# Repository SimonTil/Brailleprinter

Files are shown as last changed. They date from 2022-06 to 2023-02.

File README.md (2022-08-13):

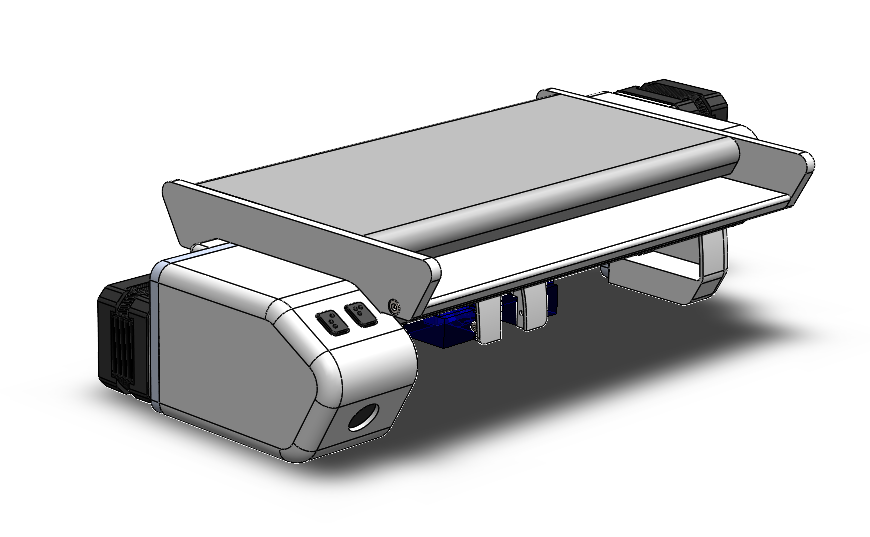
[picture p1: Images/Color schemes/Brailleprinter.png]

# Project brailleprinter
_Versie 1.0 door Simon Tillema_

Nederland kent zo'n 250.000 mensen met een visuele beperking. Ongeveer 3000 mensen gebruiken braille om te communiceren.
Tegenwoordig zijn de digitale middelen voor deze groep mensen enorm, waardoor braille op papier niet veel meer voorkomt.
Het gevolg daarvan is dat middelen om braille te 'schrijven' beperkt zijn. Braille op papier wordt voornamelijk gebruikt
waar digitale middelen (zoals brailleleesregel) niet toegepast kunnen worden. Denk daarbij aan stukken tekst die tijdens
een speciale gebeurtenis voorgelezen moeten worden, muziekteksten om te zingen, (liefdes)brieven, boeken, gedichten etc.    
Het 'schrijven' van braille op papier kan op 3 manieren:
1. met een reglette en prikpen;
2. met een brailletypemachine;
3. met een brailleprinter.

De focus binnen dit project ligt op die laatste. Commercieel beschikbare brailleprinters beginnen zo rond de €3000,- Dat
is voor de particulier praktisch onbetaalbaar. Daarom is besloten een goedkope open source brailleprinter op de markt te
zetten. Met een waarde van ongeveer een tiende van commercieel verkrijgbare apparaten is dit een echte game-changer. Het
apparaat moet door ieder die een beetje technische aanleg heeft in elkaar gezet kunnen worden.

## Hoe werkt de brailleprinter
De brailleprinter wordt geleverd met een softwarepakket dat teksten naar de brailleprinter stuurt. Daarmee kan men tekst
omzetten in braille en uit laten printen.
### Brailleprinter aansluiten
De brailleprinter bevat twee kabels: een stroomkabel, die 12V (48W) vraagt, en een USB-kabel naar de computer. De kabels
zitten niet strak vast in de brailleprinter. Belangrijk is dus om er niet te hard aan te trekken. Steek de stroomadapter
in het stopcontact en de USB-kabel in de computer. Vervolgens kan het programma gestart worden. Wanneer de kabel niet op
de computer is aangesloten, draait het programma wel, maar kan logischerwijs niet geprint worden. Zodra de stroomadapter
is aangesloten, geeft de printer een piepje. Nog een piepje klinkt als de USB-kabel wordt aangesloten. De brailleprinter
is nu klaar voor gebruik.
### Programma installeren
Moet nog gedaan worden!

## Licentie
(NL) Dit project is gelicenseerd onder de Creative Commons licentie (CC BY-NC-SA). Dat houdt in:  
Je bent vrij om:  
- **het werk te delen** - te kopiëren, te verspreiden en door te geven via elk medium of bestandsformaat;  
- **het werk te bewerken** - te remixen, te veranderen en afgeleide werken te maken.  

onder de volgende voorwaarden:  
- **Naamsvermelding:** De gebruiker dient de maker van het werk te vermelden, een link naar de licentie te plaatsen en aan
te geven of het werk veranderd is. Je mag dat op redelijke wijze doen, maar niet zodanig dat de indruk gewekt wordt dat
de licentiegever instemt met je werk of je gebruik van het werk;  
- **NietCommercieel:** Je mag het werk niet gebruiken voor commerciële doeleinden;  
- **GelijkDelen:** Als je het werk hebt geremixt, veranderd, of op het werk hebt voortgebouwd, moet je het veranderde
materiaal verspreiden onder dezelfde licentie als het originele werk;   
- **Geen aanvullende restricties:** Je mag geen juridische voorwaarden of technologische voorzieningen toepassen die
anderen er juridisch in beperken om iets te doen wat de licentie toestaat.  

_Zie ook de [website van Creative Commons](https://creativecommons.org/licenses/by-nc-sa/3.0/nl/deed.nl)._  

(EN) This project is licensed under the Creative Commons License (CC BY-NC-SA). That means:  
you are free to:  
- **Share** - copy and redistribute the material in any medium or format;  
- **Adapt** - remix, transform, and build upon the material.  

under the following terms:  
- **Attribution:** You must give appropriate credit, provide a link to the license, and indicate if changes were made. You
may do so in any reasonable manner, but not in any way that suggests the licensor endorses you or your use;  
- **NonCommercial:** You may not use the material for commercial purposes;  
- **ShareAlike:** If you remix, transform, or build upon the material, you must distribute your contributions under the same
license as the original;  
- **No additional restrictions:** You may not apply legal terms or technological measures that legally restrict others from
doing anything the license permits.  

_See also the [website of Creative Commons](https://creativecommons.org/licenses/by-nc-sa/3.0/nl/deed.en)._  

## Help de ontwikkeling 
Vindt u dit een mooi project en wilt u helpen om dit project een toekomst te geven? Dat kan!
Bent u handig met programmeren (C++/C#), 3D-tekenen (SolidWorks), prototypen, of PCB-design? Neem dan gerust contact op,
zodat we samen kunnen kijken wat u kunt betekenen voor dit project.  
Wilt u helpen, maar bent u niet technisch aangelegd? Geen probleem! Daar is ook een oplossing voor! Middels een (kleine)
financiële bijdrage kunnen de ontwikkelaars meer tijd vrijmaken om te werken aan dit project! Overmaken kan via de link:
[paypal.me/drawingsimon](paypal.me/drawingsimon).  
Licentie: dit project is gelicenseerd onder de Creative Commons licentie (CC BY-NC-SA) en mag, met vermelding van auteur
onder dezelfde licentie niet-commercieel gebruikt worden.  
Ik verzoek u vriendelijk de auteur op de hoogte te stellen van het gebruik van (delen van) het project, bijvoorbeeld via
een e-mail aan [simontillema@gmail.com](mailto:simontillema@gmail.com), of op andere wijze.

## Met dank aan
Mijn speciale dank gaat uit naar mijn vriendin Anne die mij geweldig heeft gesteund in dit project.  
Verder wil ik Michael bedanken die mij meerdere malen wist te motiveren om door te gaan.

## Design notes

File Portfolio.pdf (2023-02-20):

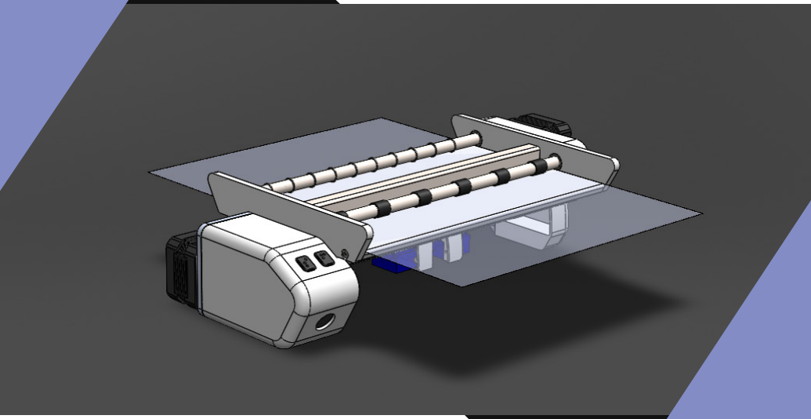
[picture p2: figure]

# PROJECT BRAILLE PRINTER

Sept. 16, 2022 | By Simon Tillema

### PAGE

# A Braille Printer?

### Commercially available braille printers are expensive and often large in

size. There are just a few open-source models available, which are large, slow, unreliable, and do not produce clear braille.

### The model I developed is better in all respects. it can print all six dots at once; it prints clearly readable braille; is very reliable and is built as compact as possible. With a simple computer program, everyone can use the

plug-and-play printer.

### I also developed this braille printer for my fiancée in light of her visual impairment. This apparatus makes it easier for me to have written communication with her. Her feedback was indispensable throughout the develop-

ment process.

### The first text printed (with the first prototype) for my girlfriend was some-

thing along the lines of Do you want to marry me? Fortunately she said YES.

You can follow this project on GitHub! https://github.com/SimonTil/Brailleprinter

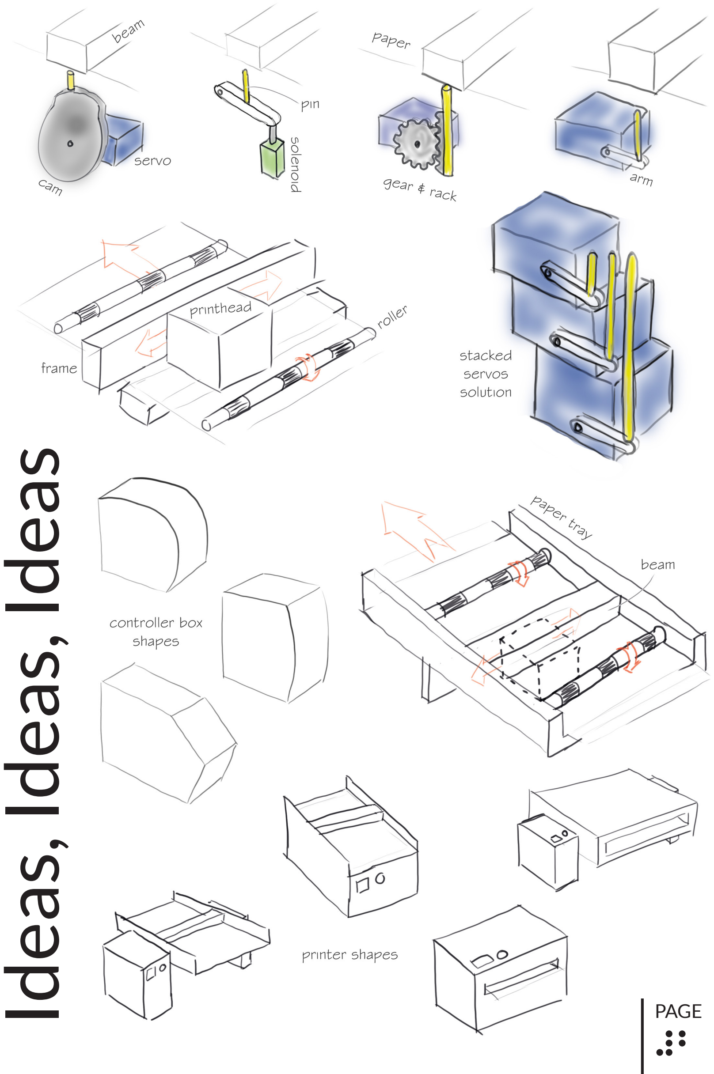
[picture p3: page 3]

# Ideas, Ideas, Ideas

### PAGE PAGE

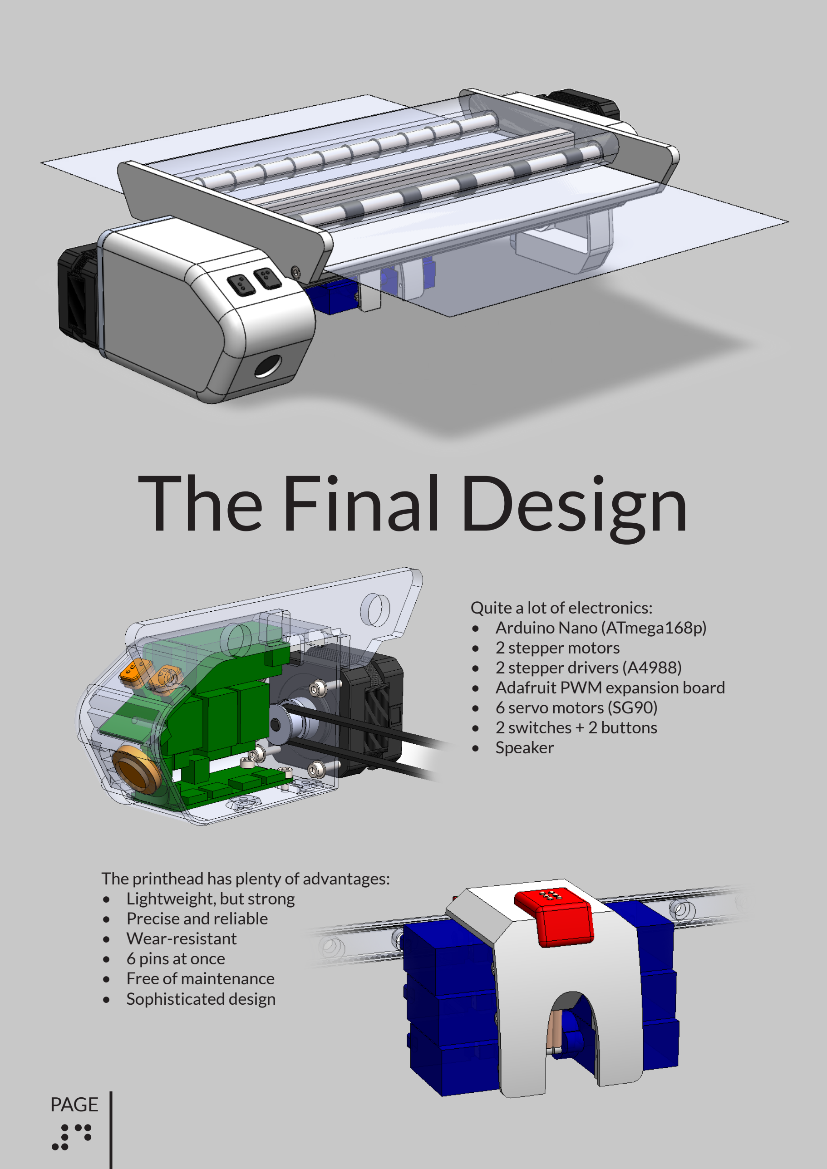
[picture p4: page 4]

Quite a lot of electronics:
- Arduino Nano (ATmega168p)
- 2 stepper motors
- 2 stepper drivers (A4988)
- Adafruit PWM expansion board
- 6 servo motors (SG90)
- 2 switches + 2 buttons
- Speaker

The printhead has plenty of advantages:
- Lightweight, but strong
- Precise and reliable
- Wear-resistant
- 6 pins at once
- Free of maintenance
- Sophisticated design

# The Final Design

# PAGEManufacturing

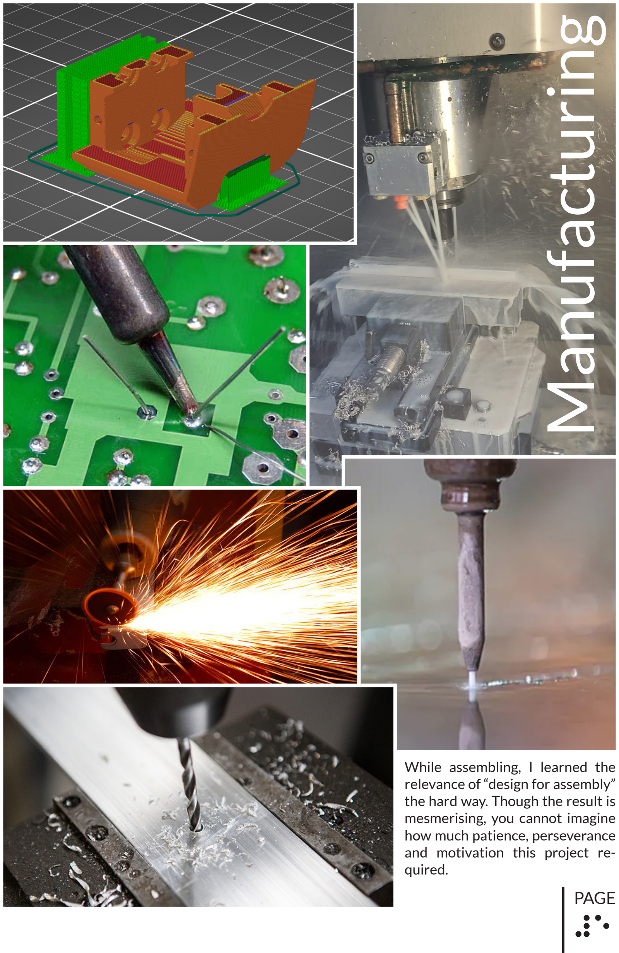
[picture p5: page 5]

While assembling, I learned the relevance of “design for assembly” the hard way. Though the result is mesmerising, you cannot imagine how much patience, perseverance and motivation this project re

quired.

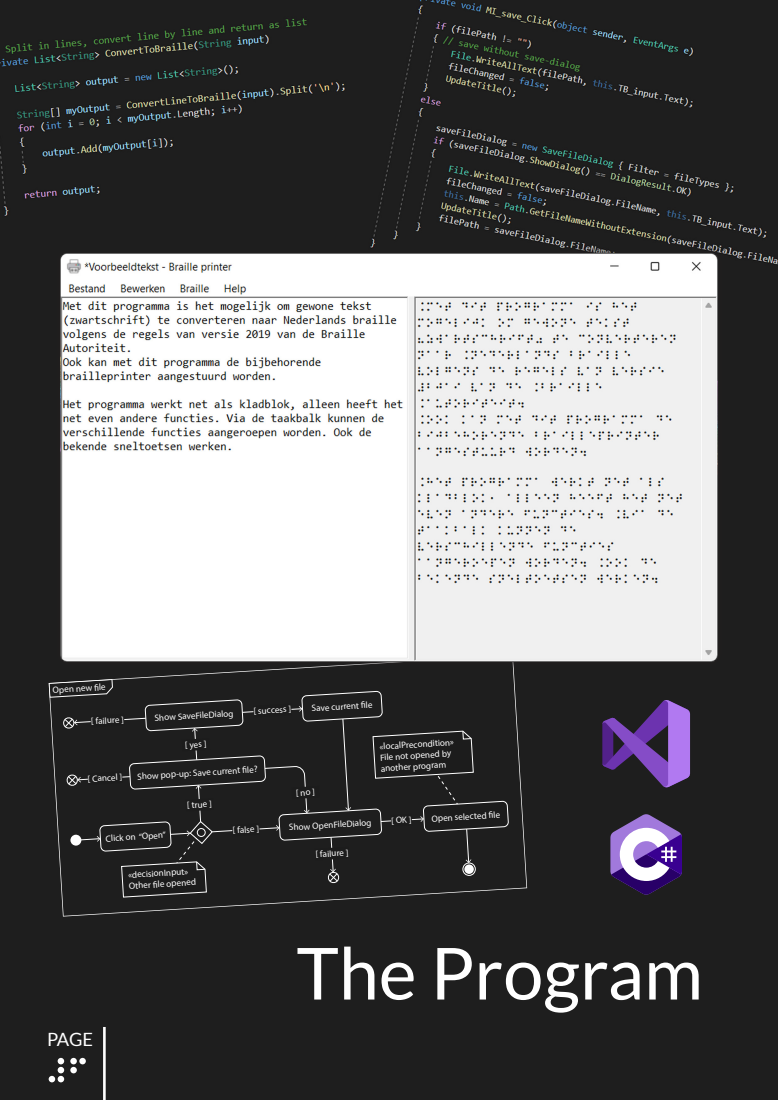
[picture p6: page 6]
«decisionInput»; [ true ]; [ Cancel ]; Show SaveFileDialog; [ yes ]; [ failure ]; «localPrecondition»; another program; The Program

Open new le

Save current le [ success ]

File not opened by

Show pop-up: Save current le?

[ OK ] Open selected le

Show OpenFileDialog [ false ]

Click on “Open”

Other le opened

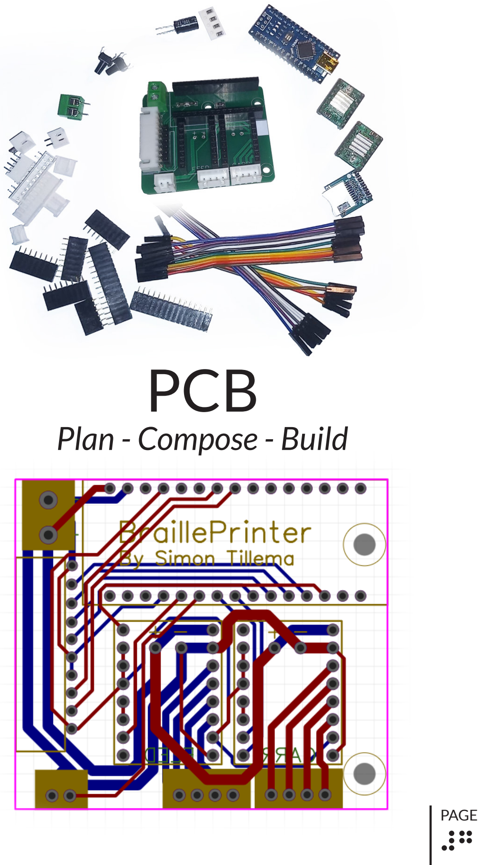
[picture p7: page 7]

# PCB

# Plan - Compose - Build

# Never Give Up!

Servos became glowing hot!
Due to the incorrect power supply, way too much current was provided to the servos, causing them to overheat. The temperature was far beyond the safe operation temperature. Within two minutes, the servos rose to an untouchable temperature. The solution to this problem was to use a DC/DC-module with lower specification.

Arduino was backwards oriented on PCB
A stupid mistake I will never make again: the pin orientation of the Arduino was reversed on the custom PCB, causing the connector to face inward instead of to the back. The only solution was to redesign the PCB.

Installation of open loop belt hard to install Though the idea was good (no restriction on belt length), in practice is caused me twice a headache - during assembly, and when a servo had to be replaced. The solution I came up with uses a closed loop belt. This makes installation much easier. The only required modification was a different frame plate design.

Beam with holes not properly aligned Because a few constructive parts were 3D printed, the alignment of the beam relative to the printhead was misaligned about 0,3 mm, which is way too much. Allowable tolerance is around 0,05 mm, since the pins do not have a lot of play. This issue was fixed by heating the 3D printed part and cheating them in the right position.

Servos not powerful enough
To emboss a dot in paper, quite some force is required. The maximum torque the used SG90 servos can provide, proved to be insufficient in this case. The solution will be to decrease the length of the arm attached to the rotor.

Servos ‘shock’ at boot
When the servos are powered at a boot, they tend to move clockwise, no matter in which position they are. This resulted in 3 pins penetrating the beam, and 3 pins falling out of the printer. This is an issued that cannot be solved without the use of better servos. The solution I came up with is to reduce the time from initial boot until first signal. Pins are still falling out sometimes.

Arduino not suitable for braille conversion The used Arduino with ATmega168p chip is very limited on possibilities. Converting regular text to braille is impossible for the Arduino. This requires too much memory. The only solution was to let the computer do the calculations. As a result, I had to to rewrite the entire program code, communication protocol, and interface of the program. After that, the Arduino uses about 70% of its memory. The second optimization reduced the file by more than 50%! Due to a lot of fiddling in the code, it became very inefficient.

Motor for paper feed not powerful enough When all features are on high-power mode, the available power need to be divided over 6 servos and 2 steppers. This caused the paper feed stepper to be not strong enough to feed the paper. The solution was quite simple; turn off the power for the other motors when paper is fed.

Arduino unable to play sound
Without external module, an Arduino cannot play voice messages (like “Welcome! Please load a new paper into the printer...”) on a speaker. The solution was to use some standard signals instead of voice messages. Beep, beep, beep, and the user knows the printer requires attention. The program now contains 4 different tunes and the used frequences according to ISO 16.

I had to solve 1001 problems. Below a list of the most interesting ones:

# #OpenToWork

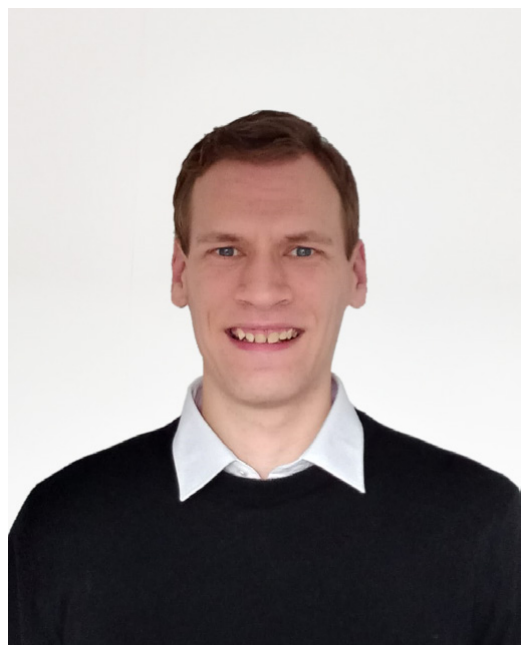
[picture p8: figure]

Ing. Simon H. Tillema
Weertmanplein 6
3815 XJ Amersfoort
The Netherlands

+31 (0)6 313 272 37
simontillema@gmail.com

linkedin.com/simon-tillema/

Download my resume at:
tinyurl.com/resumeSimon

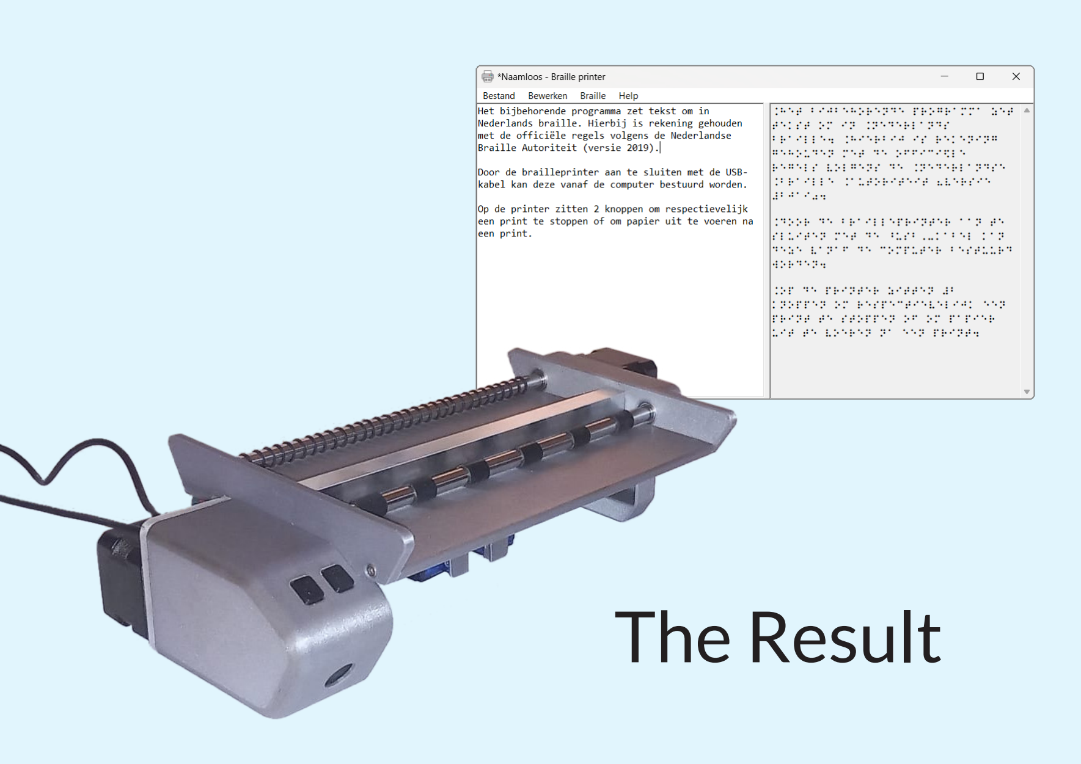
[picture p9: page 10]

# The Result

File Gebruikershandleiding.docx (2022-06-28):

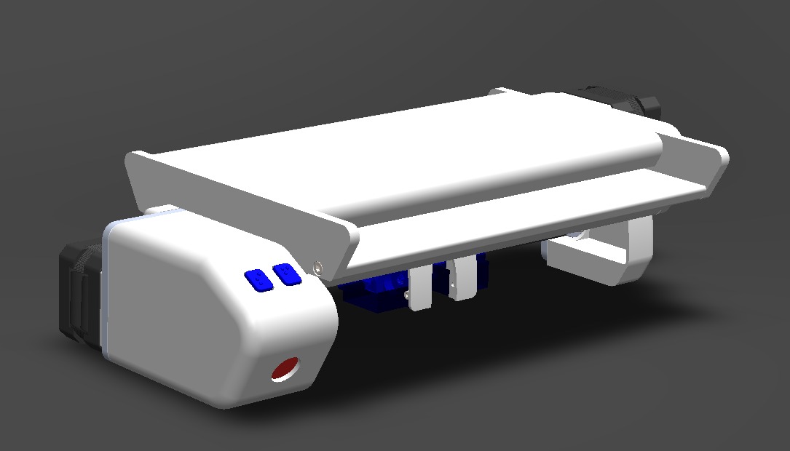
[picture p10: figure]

Brailleprinter

Gebruikshandleiding

door Simon Tillema

# Algemene informatie

# Onderdelen

# Eerste gebruik

# Periodiek onderhoud

# FAQ

# Helpen met de ontwikkeling

# Licentie

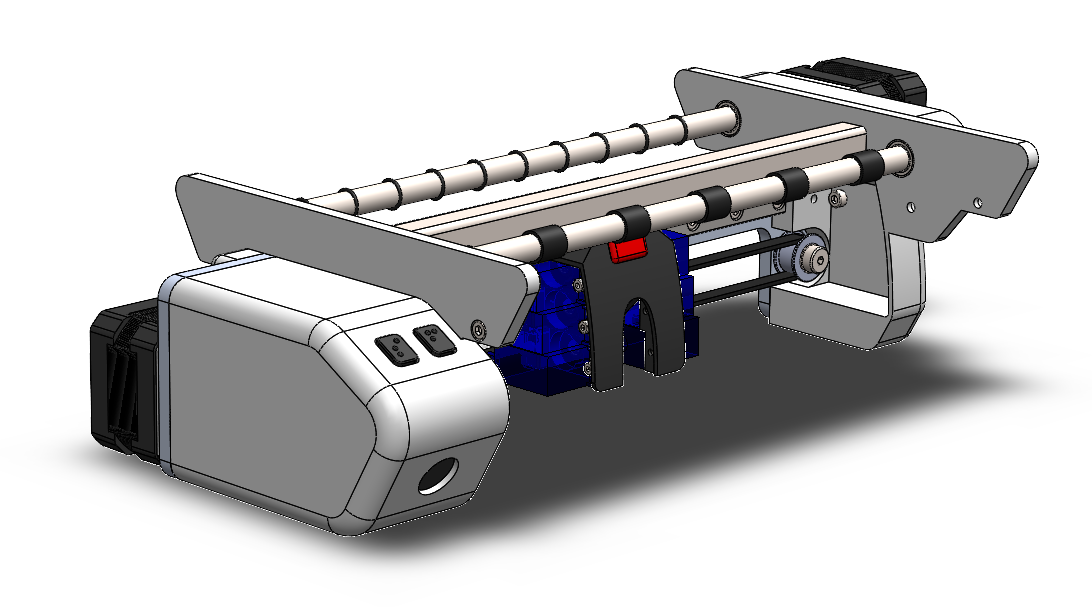
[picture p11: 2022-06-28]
Images/Parts/Without papertray.png

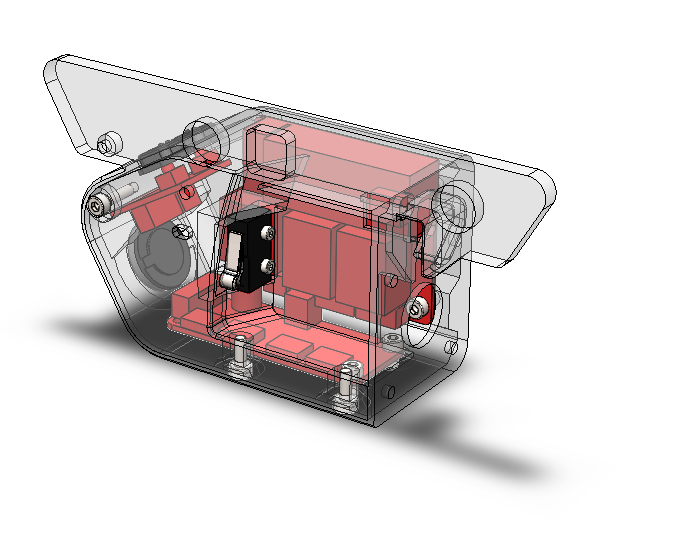
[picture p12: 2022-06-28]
Images/Parts/Electronics box.png

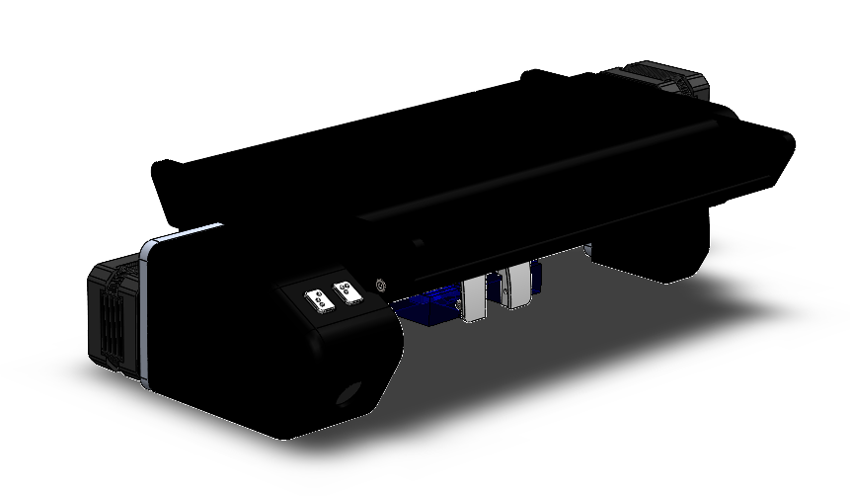
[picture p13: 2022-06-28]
Images/Color schemes/Black.png

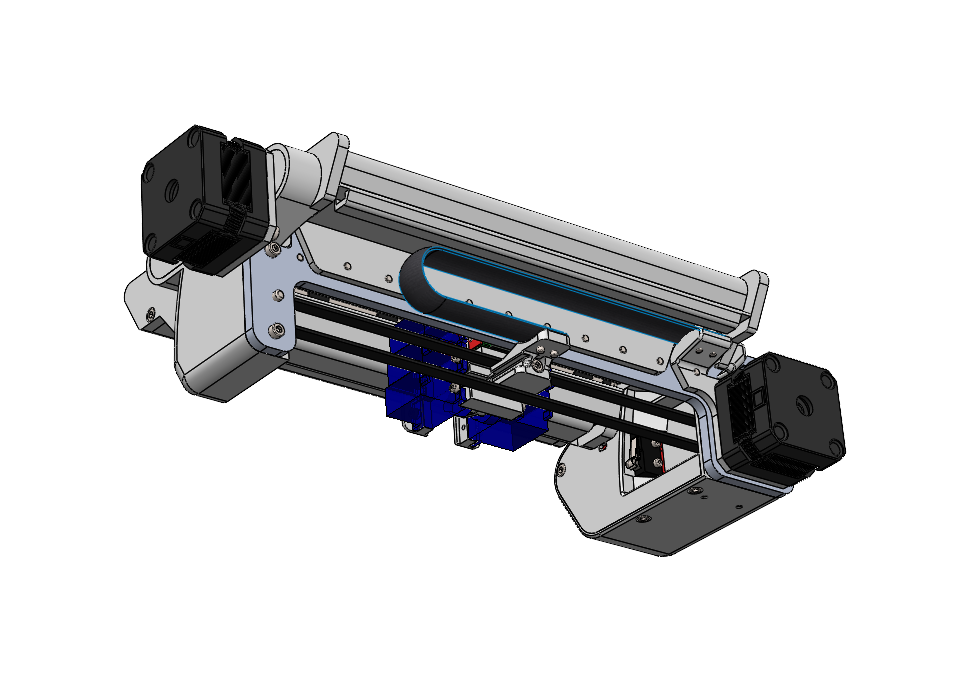
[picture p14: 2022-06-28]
Images/Different views/Isometric view back.png

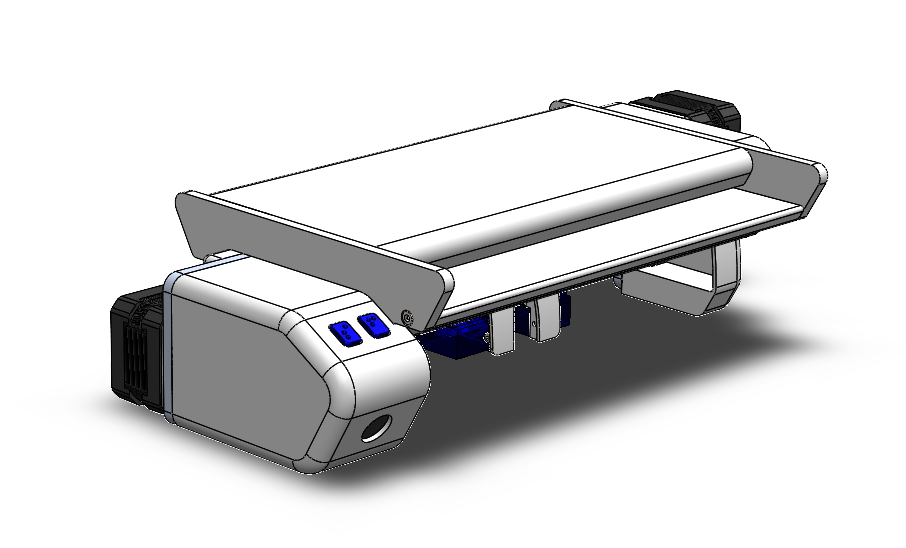
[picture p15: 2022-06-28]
Images/Color schemes/Blue.png

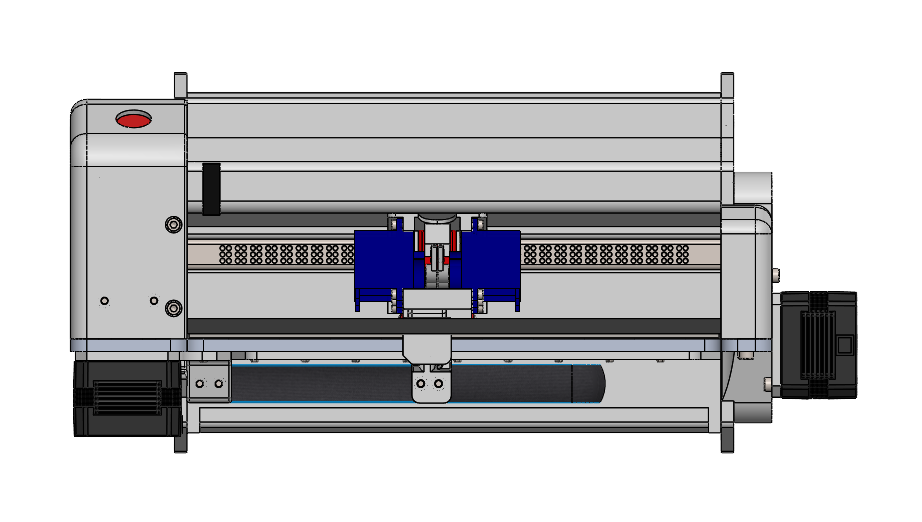
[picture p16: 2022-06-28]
Images/Different views/Bottom view.png

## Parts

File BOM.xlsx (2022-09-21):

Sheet: Blad1
Bill of Materials
Brailleprinter
No. | Name | Dimensions | Material | Quantity | Where to purchase? | Price | Notes
Frame parts
001 | Frame plate | 276,5mm x 61,3mm x 5mm | Aluminium | 1 | Custom made |  | To be CNC'ed
002 | MGN9C linear rail and block | 208,9mm - first hole at 5,7mm | Stainless steel | 1 | https://www.aliexpress.com/item/1005004535281832.html | €11.78 | Rail and block
003 | Motor plate | 61,5mm x 53,5mm x 20,2mm | PETG | 1 | Custom made |  | To be 3D-printed
004-1 | Paper tray (front) | 210,5mm x 53mm x 20mm | PETG | 1 | Custom made |  | To be 3D-printed
004-2 | Paper tray (back) | 210,5mm x 63,3mm x 22mm | PETG | 1 | Custom made |  | To be 3D-printed
Electronic box
101-1 | Electronic box (outer shell) | 150mm x 78,3mm x 46mm | PETG | 1 | Custom made |  | To be 3D-printed
101-2 | Electronic box (inner shell) | 101,8mm x 57,3mm x 21,5mm | PETG | 1 | Custom made |  | To be 3D-printed
102 | Button | 14mm x 11,5mm x 5,6mm | PETG | 2 | Custom made |  | 2 different models, to be 3D-printed
103 | Main PCB | 57mm x 46,8mm x 1,6mm | PCB | 1 | JLCPCB | €12.21 | Custom made with gerber files
104 | Button PCB | 28mm x 22mm x 1,6mm | PCB | 1 | JLCPCB |  | Custom made with gerber files
Motion system
201 | Stepper motor | Nema 17 - 33mm | - | 2 | https://www.omc-stepperonline.com/nema-17-unipolar-1-8deg-32ncm-45-3oz-in-0-4a-12v-42x42x48mm-6-wires-17hs19-0406s | €24.00
202 | 2GT pulley (driving) | 20T - 5mm bore | Aluminium | 1 | https://www.aliexpress.com/item/1005002226516848.html | €1.14
203 | 2GT pulley (driven) | 20T - 5mm bore | Aluminium | 1 | https://www.aliexpress.com/item/1005003068711960.html | €0.70
204 | 2GT pulley (driving) | 20T - 8mm bore | Aluminium | 2 | https://www.aliexpress.com/item/1005003068711960.html | €0.82
205 | 2GT pulley (driving) | 16T - 5mm bore | Aluminium | 1 | https://www.aliexpress.com/item/1005003068711960.html | €0.82
206 | Closed loop 2GT belt | 524mm x 6mm | - | 1 | https://www.aliexpress.com/item/1005004107020953.html | €2.23 | 262T / 564mm
207 | Closed loop 2GT belt | 200mm x 6mm | - | 1 | https://www.aliexpress.com/item/1005002575803340.html | €1.64 | 100T / 200mm
Paper feeding
301-1 | Side block | 150mm x 78,3mm x 20mm | PETG | 1 | Custom made |  | To be 3D-printed
301-2 | Side block | 93,9mm x 41mm x 7mm | PETG | 1 | Custom made |  | To be 3D-printed
302 | MR128ZZ bearing | 14mm x 3,5mm (ID 8mm) |  | 4 | https://www.aliexpress.com/item/1005004192087723.html | €4.05
303 | HK050908 bearing | 9mm x 8mm (ID 5mm) |  | 1 | https://www.aliexpress.com/item/1005002675145083.html | €1.94
304 | Smooth rod | Ø8mm x 229,5mm | Stainless steel | 2 | Local | €0.00
305 | Rubber tube | 9mm x 2mm - 64mm long | Rubber | 1 | https://www.aliexpress.com/item/1005001683018083.html | €2.18
306 | Rubber rings | OD 9mm x 1mm | Rubber | 10 | https://www.aliexpress.com/item/32974016348.html | €1.38
307 | Counter block | 218,5mm x 12mm x 12mm | Stainless steel | 1 | Custom made |  | To be CNC'ed
308 | Cap | 210,5mm x 107mm x 15,5mm | PETG | 1 | Custom made |  | To be 3D-printed
Carriage
401-1 | Carriage | 46,5mm x 43,8mm x 39mm | PETG | 1 | Custom made |  | To be 3D-printed
401-2 | Carriage wire guide | 37,4mm x 19mm x 13,1mm | PETG | 1 | Custom made |  | To be 3D-printed
402 | Servo motor | 6g (wire near bottom) | - | 6 | https://www.aliexpress.com/item/4000903734519.html | €17.20
403 | Servo arm | 14,5mm x 10mm x 4,3mm | PETG | 6 | Custom made |  | To be 3D-printed, 3 mirrored
404 | Brass tube | 2,5mm x 0,45mm x 120mm | Brass | 1 | Local | €0.00 | Cut: 2x 32,5mm, 2x 20mm, 2x 7,5mm
405 | Brass wire | 1,5mm x 165mm | Brass | 1 | Local |  | Cut: 2x 40mm, 2x 27,5mm, 2x 15mm
406 | Spring | 5mm x 2mm x 0,2mm | Stainless steel | 6 | https://www.aliexpress.com/item/1005002500007558.html | €5.51
407 | Printhead insert | 17,8mm x 15mm x 10mm | Aluminium (anodised) | 1 | Custom made |  | To be CNC'ed
408 | Tape measure band | 255mm | - | 1 | Custom made |  | Cut on length, drill holes, round corners
409 | Woven cable sleeve | 255mm x 14mm | - | 1 | https://www.aliexpress.com/item/4000699992070.html | €1.30 | Length dependent on expansion ratio
Electronic components
501 | Power adapter | 12V/4A | - | 1 | https://www.aliexpress.com/item/32295008205.html | €5.96 | EU plug
502 | Limit switch | 20,1mm x 10,6mm x 6,3mm | - | 2 | Local | €0.00 | Buy straight and bend, or buy curved
503 | DCDC step-down converter | 5V/4A | - | 1 | https://www.aliexpress.com/item/1005003796432605.html | €1.97 | 12V input
504 | Speaker 8Ω/1W | 20mm | - | 1 | https://www.aliexpress.com/item/32963097808.html | €0.59
505 | Servo driver module | 16 pins | - | 1 | https://www.aliexpress.com/item/4001068352842.html | €4.06
506 | Arduino Nano | chip: 328p | - | 1 | https://www.aliexpress.com/item/32647196840.html | €5.30 | With soldered pins
507 | DRV8825 stepper driver | - | - | 2 | https://www.aliexpress.com/item/1005001639031308.html | €1.61
508 | Micro SD reader | Mini | - | 1 | https://www.aliexpress.com/item/1005002530096777.html | €0.52 | Smallest version with 6 pins
509 | Screw terminal |  |  | 1 | https://www.aliexpress.com/item/1005001341135808.html | €1.10 | Color not important
510 | SMD resistor | 1206 | - | 6 | https://www.aliexpress.com/item/1005001794416354.html | €0.63 | 3x 1kΩ, 3x 2kΩ
511 | Header connector | 2,54mm pin distance | - | 7 | Local | €0.00 | 1x 6pin, 4x 8pin, 2x 15pin
512 | JST-XH connector (straight) | - | - | 3 | Local |  | 1x 6pin, 3x 4pin, 2x 2pin (male and female)
513 | JST-XH connector (curved) | - | - | 1 | https://www.aliexpress.com/item/4000029760504.html | €0.62 | 10pin (male and female)
514 | Mini button switch | 6mm x 6mm - 10mm pin | - | 2 | https://www.aliexpress.com/item/32912263133.html | €1.01
515 | Wires | 22AWG | - | - | Local | €0.00 | Different lengths
516 | Shrink tubes | Different sizes | - | - | Local
Fasteners
601 | DIN125A ring | M3 | Galvanized steel | 4 | Local | €0.00
602 | DIN912 screw | M3 x 8 | Galvanized steel | 1 | Local
603 | DIN912 screw | M3 x 12 | Galvanized steel | 12 | Local
604 | DIN912 screw | M3 x 16 | Galvanized steel | 4 | Local
605 | DIN912 screw | M2 x 6 | Stainless steel | 12 | Local
606 | DIN912 screw | M2 x 12 | Stainless steel | 2 | Local
607 | DIN912 screw | M2,5 x 10 | Stainless steel | 2 | Local
608 | DIN912 screw | M3 x 5 | Stainless steel | 6 | Local
609 | DIN912 screw | M3 x 6 | Stainless steel | 5 | Local |  | 2x head shortened to 2mm
610 | DIN912 screw | M3 x 8 | Stainless steel | 7 | Local
611 | DIN912 screw | M3 x 10 | Stainless steel | 2 | Local
612 | DIN912 screw | M3 x 12 | Stainless steel | 5 | Local
613 | DIN912 screw | M3 x 16 | Stainless steel | 0 | Local
614 | DIN912 screw | M3 x 25 | Stainless steel | 1 | Local
615 | DIN988 shim ring | 5mm x 10mm x 0,5mm | Steel | 2 | Local
616 | Shoulder screw | M4 x 5f9 x 8mm | Stainless steel | 1 | Local |  | Thread shortened to 5mm
617 | Shoulder screw | M4 x 5f9 x 10mm | Stainless steel | 1 | Local

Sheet: Blad2
DIN125A | M3 | Stainless steel | 4 | Local
DIN912 | M3 x 8 | Galvanized steel | 1 | Local
DIN912 | M3 x 12 | Galvanized steel | 10 | Local
DIN912 | M2 x 6 | Stainless steel | 12 | Local
DIN912 | M2 x 12 | Stainless steel | 2 | Local
DIN912 | M2,5 x 10 | Stainless steel | 2 | Local
DIN912 | M3 x 5 | Stainless steel | 6 | Local
DIN912 | M3 x 6 | Stainless steel | 5 | Local | 2x head shortened to 2mm
DIN912 | M3 x 8 | Stainless steel | 7 | Local
DIN912 | M3 x 10 | Stainless steel | 2 | Local
DIN912 | M3 x 12 | Stainless steel | 7 | Local
DIN912 | M3 x 16 | Stainless steel | 4 | Local
DIN912 | M3 x 25 | Stainless steel | 1 | Local
DIN988 | 5mm x 10mm x 0,5mm | Stainless steel | 2 | Local
Shoulder screw | M4 x 5f9 x 8mm | Stainless steel | 1 | Local | Thread shortened to 5mm
Shoulder screw | M4 x 5f9 x 10mm | Stainless steel | 1 | Local

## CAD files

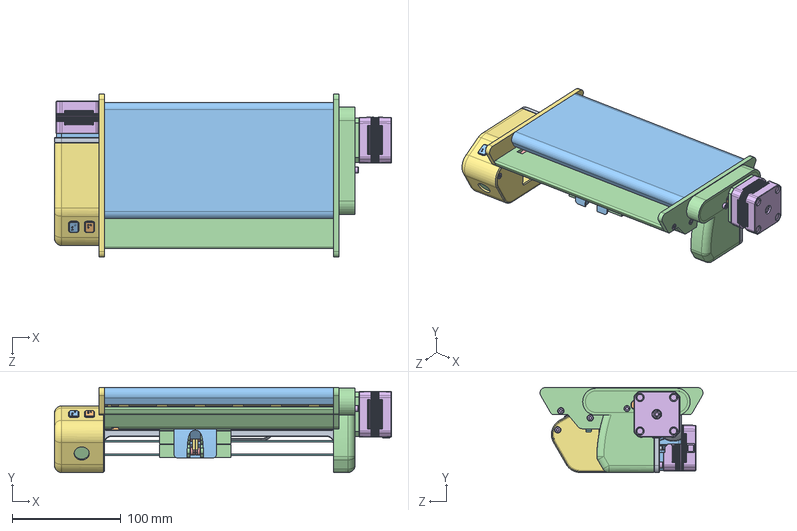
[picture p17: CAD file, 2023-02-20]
Model/CAD files/Brailleprinter.SLDASM
310.0 x 78.2 x 150.0 mm
Frame plate
Linear rail
Motor plate
Paper tray
Limit switch x 2
socket head cap screw_din x 59
Electronic box
Main PCB
Button PCB
ButtonF
ButtonS
Speaker
Servo PCB
Stepper motor x 2
2GT driving pulley x 5
Belt^Motion system
Shoulder screw
shim-support ring2_din x 2
plain washer grade a_din x 4
Side block
MR128ZZ bearing x 4
Counter block
Driving rod x 2
HK050908 bearing
Belt^Paper feeding
Shortened shoulder screw
Carriage
Servo x 6
Servo arm x 6
Printhead insert
Pin x 6
Linear block
Cable carrier
Spring x 6
Cap

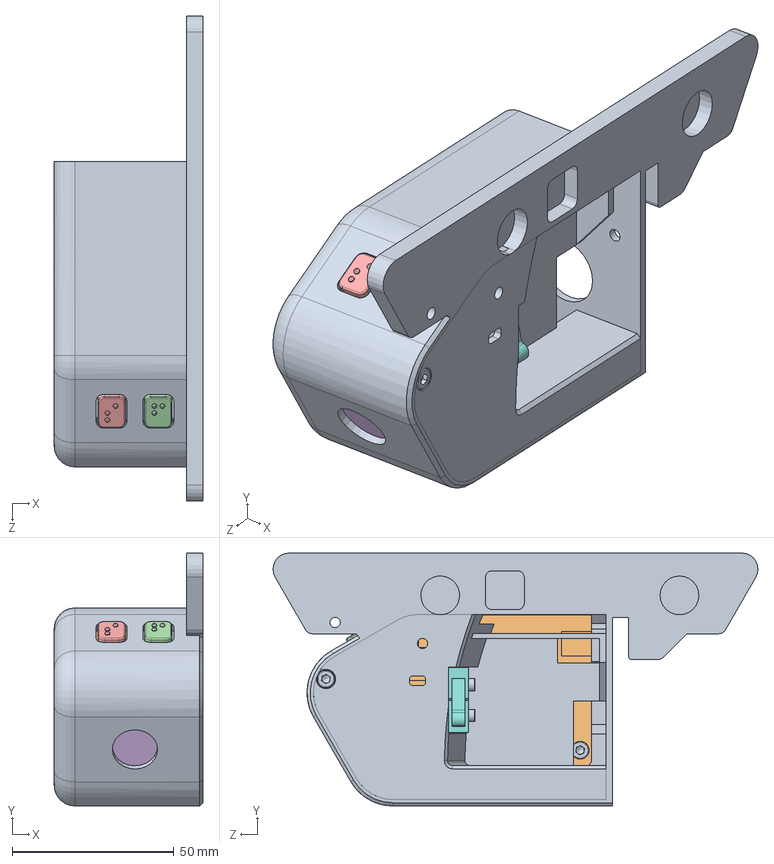
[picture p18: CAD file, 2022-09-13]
Model/CAD files/Electronics/Electronic box.SLDASM
46.0 x 78.2 x 150.0 mm
Electronic box
Main PCB
Button PCB
ButtonF
ButtonS
Speaker
Servo PCB
Limit switch
socket head cap screw_din x 10

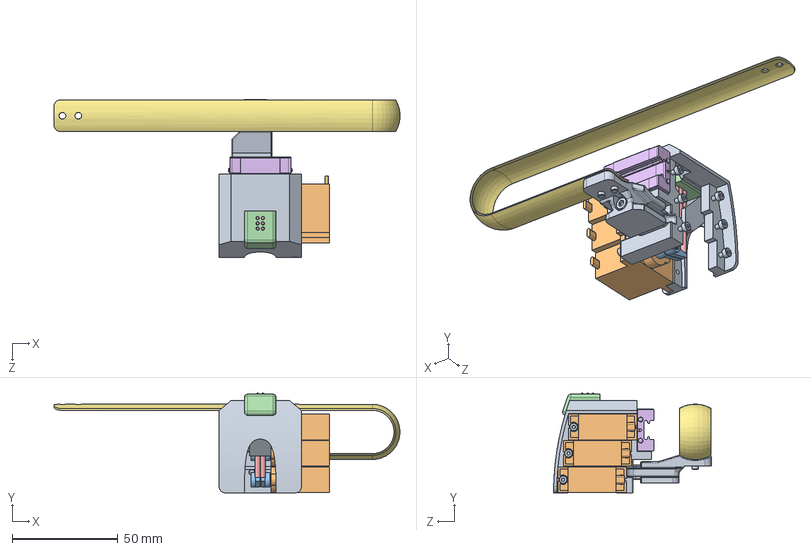
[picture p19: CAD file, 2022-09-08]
Model/CAD files/Carriage/Carriage.SLDASM
163.8 x 47.2 x 74.7 mm
Carriage
Servo x 3
Servo arm x 6
Printhead insert
Pin x 6
Linear block
Cable carrier
Spring x 6
socket head cap screw_din x 19

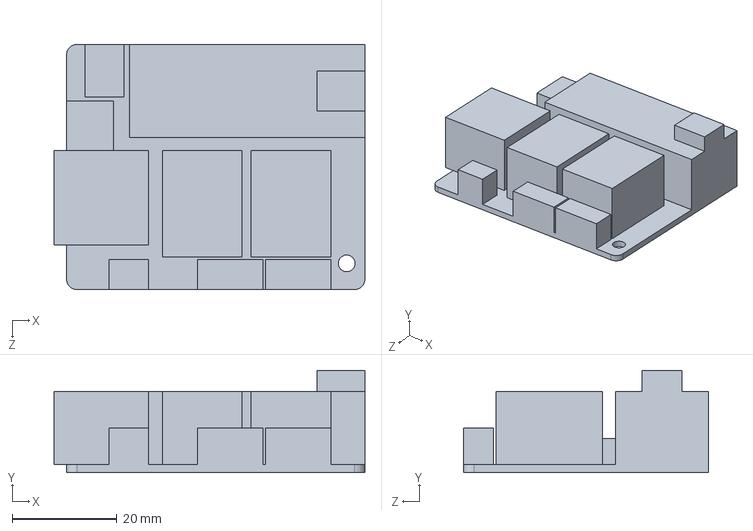
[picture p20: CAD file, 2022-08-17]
Model/CAD files/Electronics/Main PCB.SLDPRT
59.4 x 19.5 x 46.8 mm

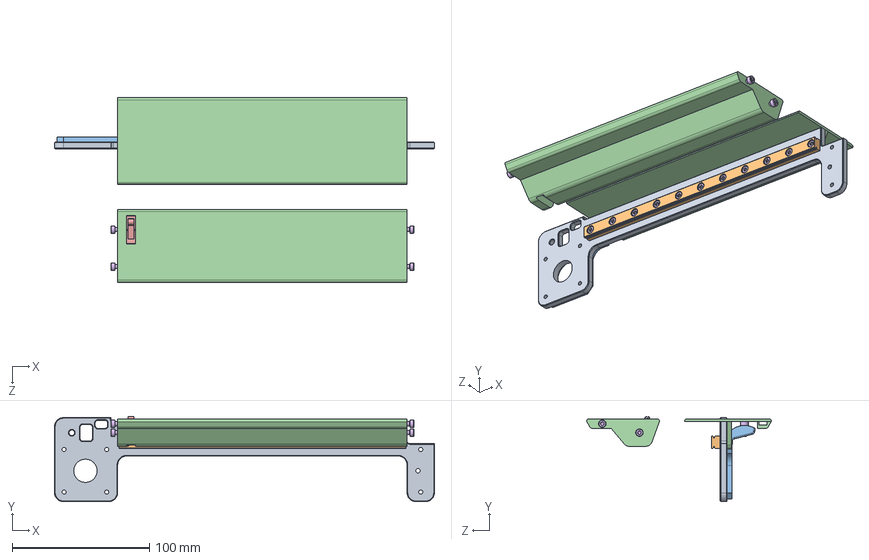
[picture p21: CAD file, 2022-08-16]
Model/CAD files/Frame/Frame.SLDASM
276.5 x 62.1 x 134.3 mm
Frame plate
Linear rail
Motor plate
Paper tray
Limit switch
socket head cap screw_din x 19

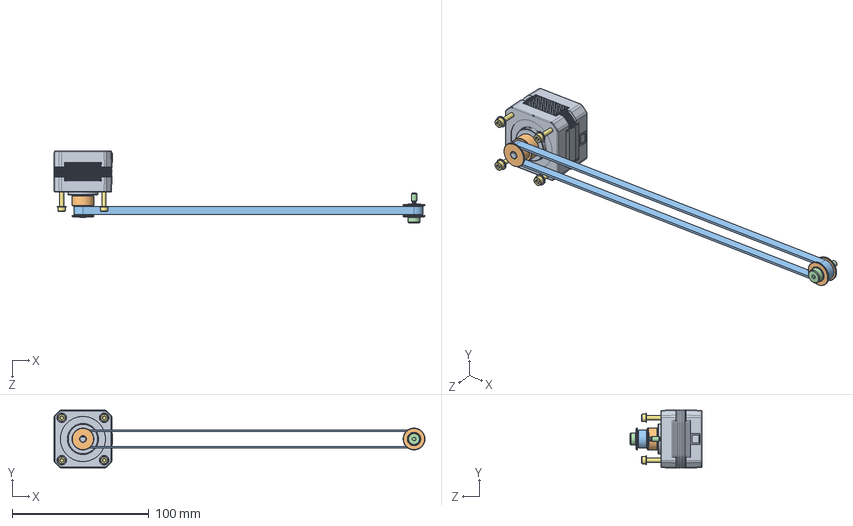
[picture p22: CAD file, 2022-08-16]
Model/CAD files/Motion system/Motion system.SLDASM
271.1 x 42.3 x 52.5 mm
Stepper motor
2GT driving pulley x 2
Belt^Motion system
Shoulder screw
shim-support ring2_din x 2
plain washer grade a_din x 4
socket head cap screw_din x 4

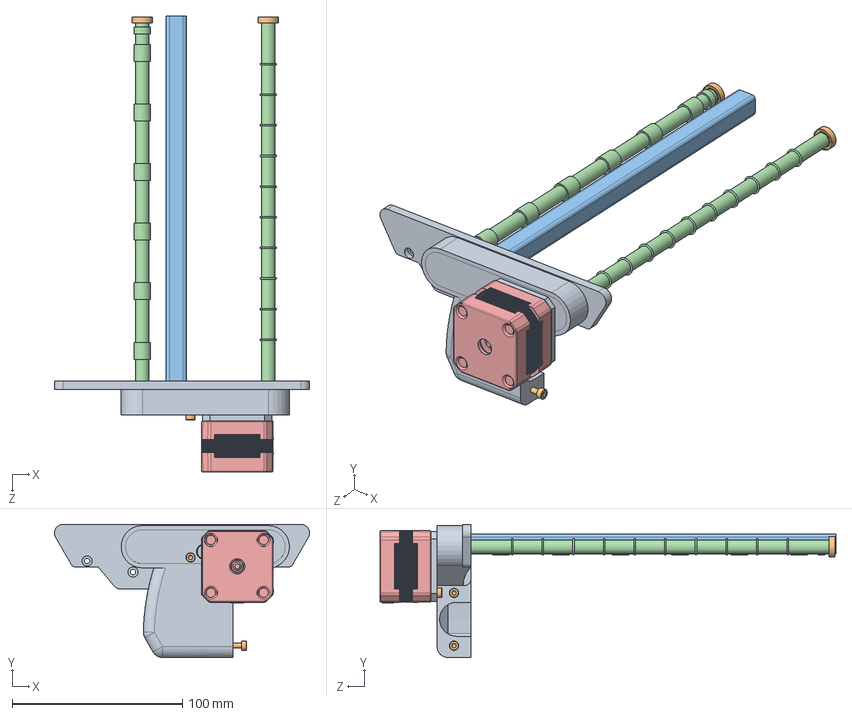
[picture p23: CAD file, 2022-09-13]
Model/CAD files/Paper feeding/Paper feeding.SLDASM
150.0 x 78.2 x 268.0 mm
Side block
MR128ZZ bearing x 4
Counter block
Driving rod x 2
Stepper motor
2GT driving pulley x 3
HK050908 bearing
Belt^Paper feeding
Shortened shoulder screw
socket head cap screw_din x 7

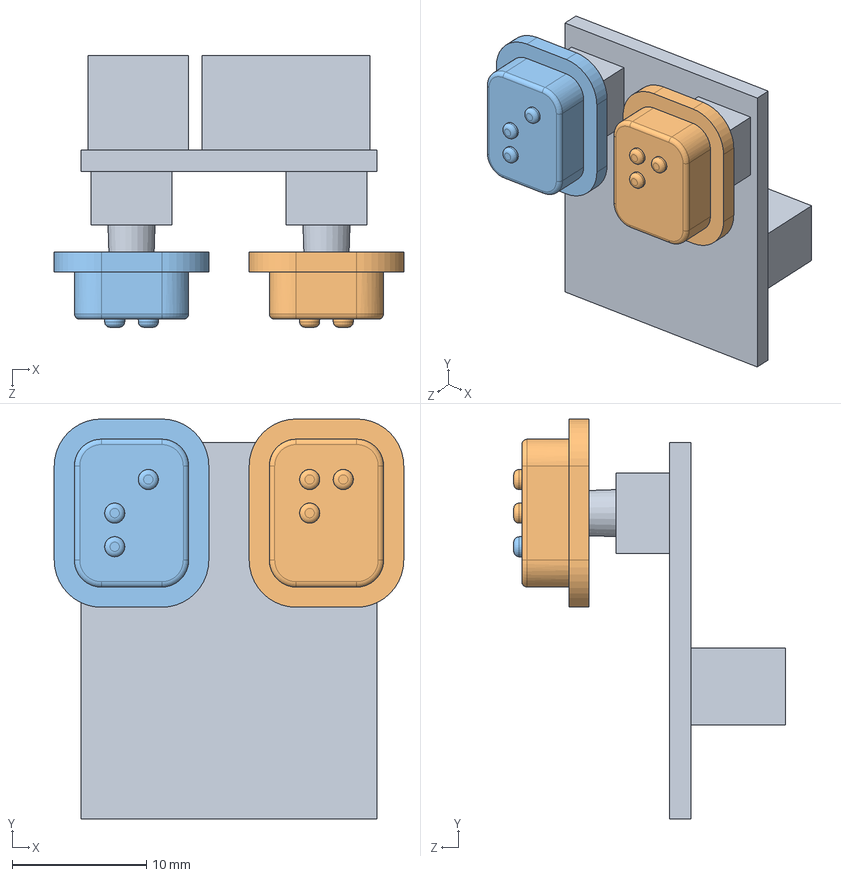
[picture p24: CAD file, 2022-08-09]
Model/CAD files/Electronics/Button PCB.SLDASM
26.0 x 29.8 x 20.2 mm
Button PCB
ButtonF
ButtonS

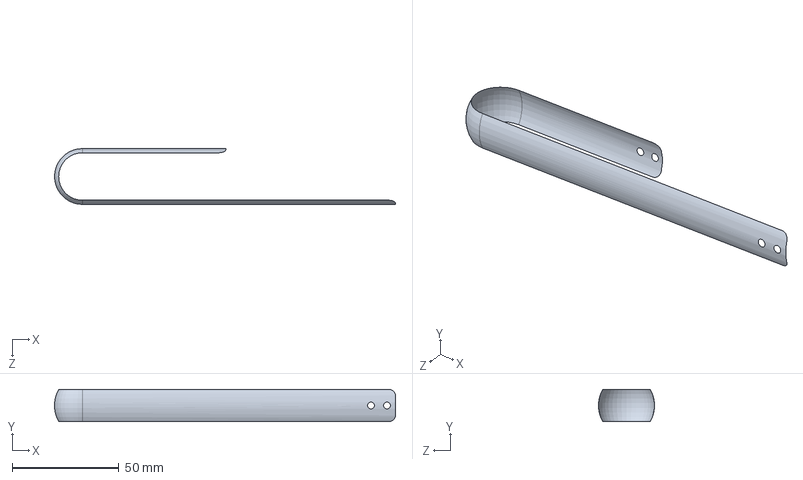
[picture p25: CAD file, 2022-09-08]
Model/CAD files/Carriage/Cable carrier.SLDPRT
159.7 x 15.0 x 26.2 mm

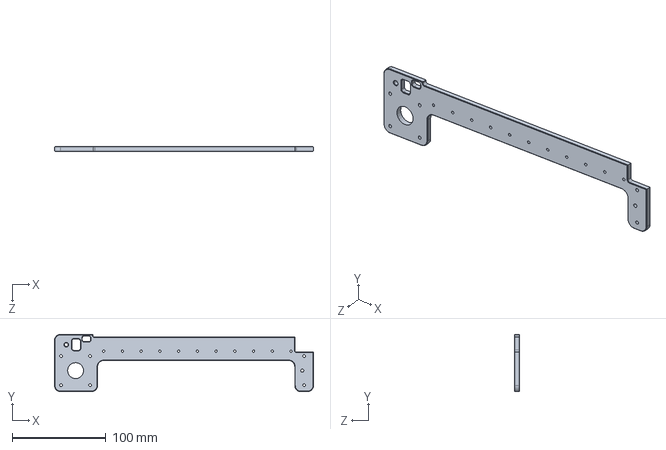
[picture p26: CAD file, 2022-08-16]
Model/CAD files/Frame/Frame plate.SLDPRT
276.5 x 61.2 x 5.00 mm

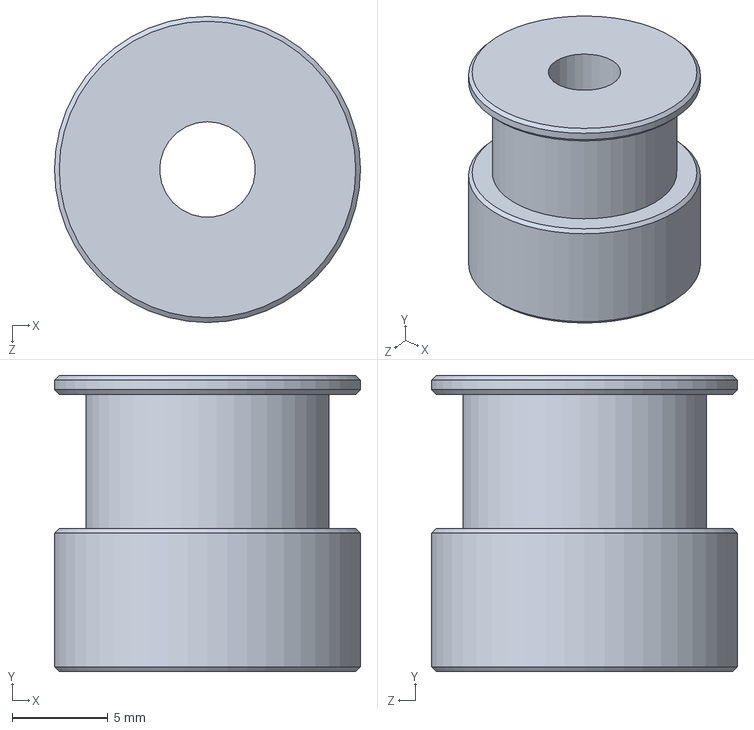
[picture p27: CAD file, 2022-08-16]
Model/CAD files/Motion system/2GT driving pulley.SLDPRT
16.0 x 15.5 x 16.0 mm

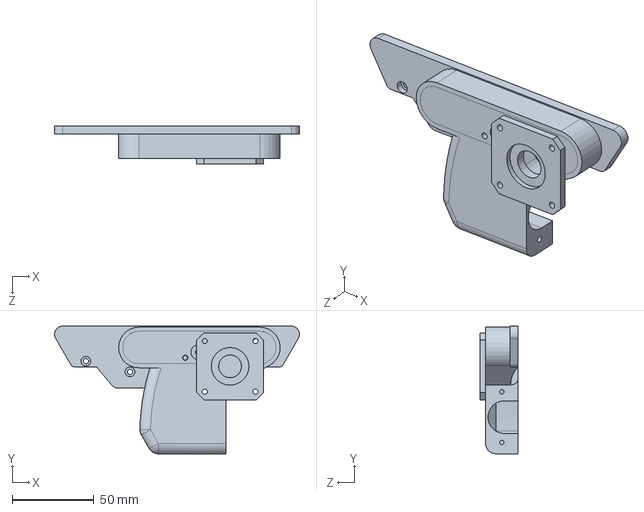
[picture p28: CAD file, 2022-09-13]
Model/CAD files/Paper feeding/Side block.SLDPRT
150.0 x 78.2 x 23.5 mm

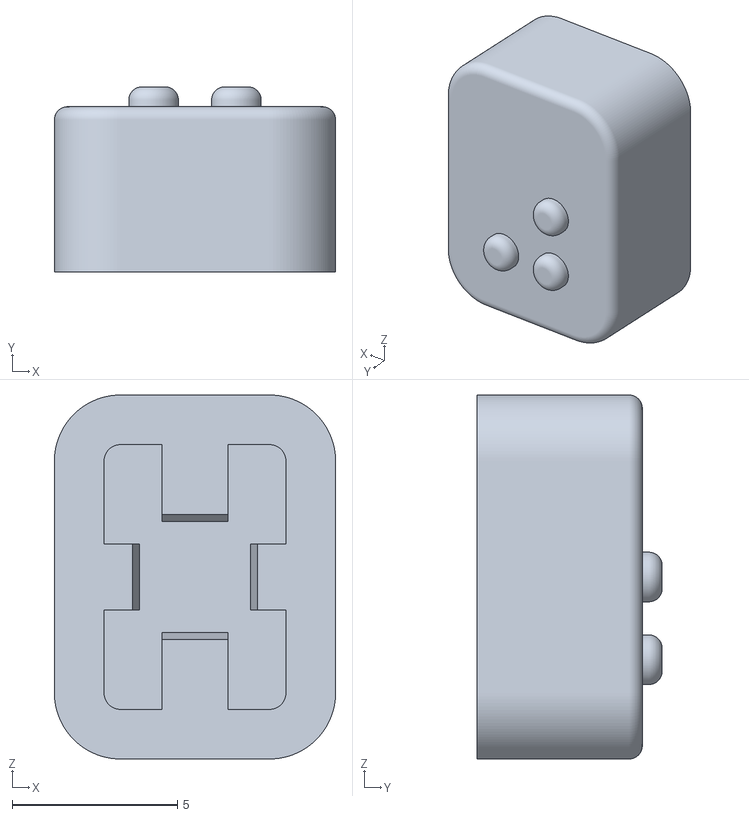
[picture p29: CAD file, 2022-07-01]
Model/Manufacturing files/3D-printing/Buttons - fit 0 extremely loose/ButtonF.STL
8.50 x 5.60 x 11.0

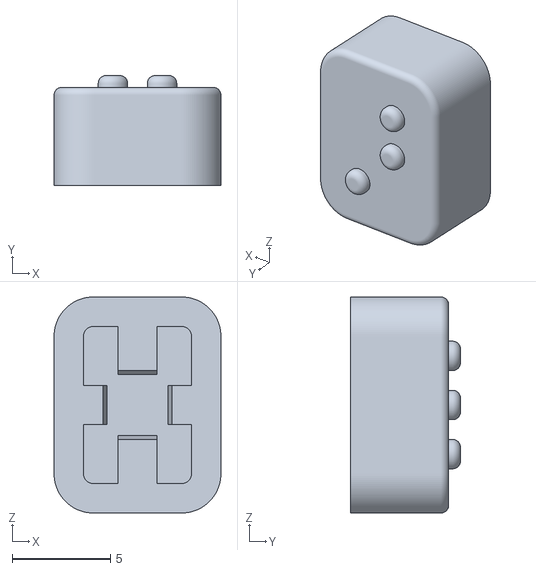
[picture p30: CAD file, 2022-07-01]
Model/Manufacturing files/3D-printing/Buttons - fit 5 tight/ButtonS.STL
8.50 x 5.60 x 11.0

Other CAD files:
Model/Manufacturing files/3D-printing/Buttons - fit 1 very loose/ButtonF.STL
Model/Manufacturing files/3D-printing/Buttons - fit 2 loose/ButtonF.STL
Model/Manufacturing files/3D-printing/Buttons - fit 3 medium loose/ButtonS.STL
Model/Manufacturing files/3D-printing/Buttons - fit 4 medium tight/ButtonF.STL
Model/CAD files/Carriage/Carriage.SLDPRT
Model/CAD files/Carriage/Linear block.SLDPRT
Model/CAD files/Carriage/Pin.SLDPRT
Model/CAD files/Carriage/Printhead insert.SLDPRT
Model/CAD files/Carriage/Servo arm.SLDPRT
Model/CAD files/Carriage/Servo.SLDPRT
Model/CAD files/Carriage/Spring.SLDPRT
Model/CAD files/Electronics/Button PCB.SLDPRT
Model/CAD files/Electronics/ButtonF.SLDPRT
Model/CAD files/Electronics/ButtonS.SLDPRT
Model/CAD files/Electronics/Electronic box.SLDPRT
Model/CAD files/Electronics/Limit switch.SLDPRT
Model/CAD files/Electronics/Servo PCB.SLDPRT
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

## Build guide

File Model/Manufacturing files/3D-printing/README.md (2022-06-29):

## 3D-printing files

Material: PLA  
Use your own settings, but for best results, see following notes:

| **File**                  | **Quantity** | **Infill** | **Color** | **Supports required?**     | **Notes**                                      |
|--------------------------|----------|-----------|-----------|----------------------------------|------------------------------------------------|
| ButtonF.STL              | 1        | 100%      | Dark grey | No                               | Print with 0.2mm nozzle, or use SLA printer    |
| ButtonS.STL              | 1        | 100%      | Dark grey | No                               | Print with 0.2mm nozzle, or use SLA printer    |
| Cap.STL                  | 1        | 10% - 30% | White     | No                               | Printer height: min. 210.5mm                   |
| Carriage_part1.STL       | 1        | 100%      | Grey      | Yes                              | Layer height 0.1mm                             |
| Carriage_part2.STL       | 1        | 100%      | Grey      | Yes                              | Layer height 0.1mm                             |
| Electronic box_part1.STL | 1        | 100%      | Grey      | Yes - force on holes for buttons |                                                |
| Electronic box_part2.STL | 1        | 100%      | Grey      | Yes                              |                                                |
| Motor plate.STL          | 1        | 100%      | Grey      | No                               | Print in PETG, ABS or other high-temp material |
| Paper tray_part1.STL     | 1        | 100%      | Grey      | No                               | Print top side on bed, print on smooth PEI     |
| Paper tray_part2.STL     | 1        | 100%      | Grey      | No                               | Print top side on bed, print on smooth PEI     |
| Servo arm.STL            | 3        | 100%      | White     | Yes                              | Print with 0.2mm nozzle, or use SLA printer    |
| Servo arm_mirrored.STL   | 3        | 100%      | White     | Yes                              | Print with 0.2mm nozzle, or use SLA printer    |
| Side block_part1.STL     | 1        | 100%      | Grey      | Yes                              |                                                |
| Side block_part2.STL     | 1        | 100%      | Grey      | Yes                              |                                                |

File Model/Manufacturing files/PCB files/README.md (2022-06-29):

## PCB files

### Where to order
You can order the custom PCB's at JLCPCB: [https://jlcpcb.com](https://jlcpcb.com/).  
Upload both files to see the price.

### Edit the files
I have used EasyEDA to create the PCB files.  
You can download EasyEDA [here](https://easyeda.com/en).  
If you are not familiar with EasyEDA, [here](https://www.youtube.com/watch?v=1e4lOJeqAc8) is a quick tutorial.  
You can import the JSON files in order to edit them.

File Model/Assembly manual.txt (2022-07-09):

Assembly order:

1. Build the carriage.
1.1. Screw the 3D-printed carriage on the linear block with 2pcs M3x5 and 2pcs M3x6.
1.2. Push the printhead insert in the carriage. Push as far as possible. Eventually use a lighter to soften the plastic.
1.3. Assemble and enter the pins. Make sure they can move free.
1.4. 

2. Build the frame.
2.1. 

3. Build the electronic box.
3.1. Guide the carriage cable and stepper cable through the hole.
3.2. Solder the carriage cable to the servo driver.
3.3. Mount the servo driver with 2pcs M3x5.

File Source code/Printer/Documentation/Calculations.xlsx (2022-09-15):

Number of steps per mm paper feed |  |  | Number of steps per mm carriage |  |  | Speed to delay
Diameter rod | 10.2 | mm | Displacement | 0.1 | mm | Required speed | 100 | mm/s
Perimeter rod | 32.04424507 | mm |  |  |  | Time to move 0,1 mm | 0.001 | s
Displacement | 1.5 | mm | Gear motor | 20 | teeth
 |  |  | Pitch belt | 2 | mm | Number of steps per sec | 8000 | steps/s
Gear rod | 20 | teeth | Distance per rev | 40 | mm
Gear motor | 16 | teeth |  |  |  | Delay per step (s) | 0.000125 | s
Ratio | 1.25 |  | Steps per rev. motor | 3200 | steps | Delay per step (ms) | 0.125 | ms
 |  |  |  |  |  | Delay per step (μs) | 125 | μs
Steps per rev. motor | 3200 | steps | Steps per 0,1 mm | 8 | steps
 |  |  |  |  |  | Half delay (μs) | 62.5 | μs
Steps per 1,5 mm | 187.2411095 | steps

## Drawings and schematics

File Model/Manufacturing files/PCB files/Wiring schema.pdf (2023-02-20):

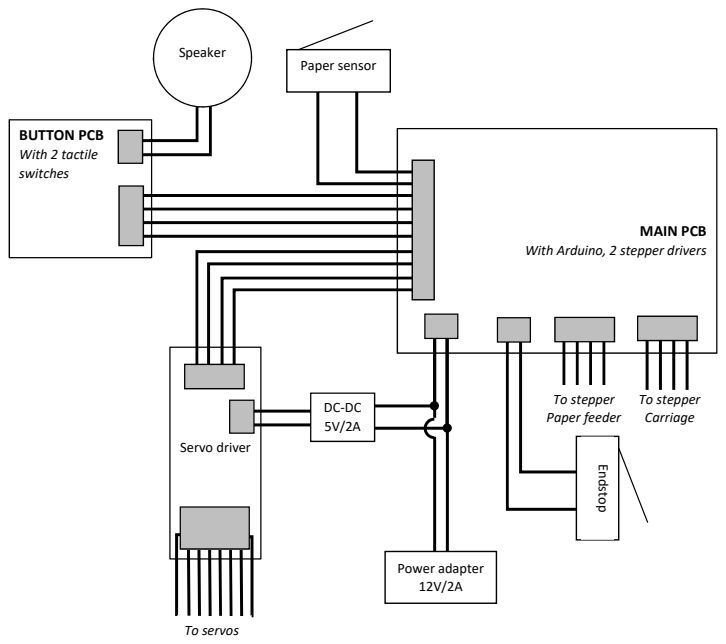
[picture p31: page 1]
MAIN PCB; BUTTON PCB With 2 tactile switches; Speaker; Servo driver; Paper sensor; Endstop; To servos; To stepper Paper feeder; To stepper; Power adapter 12V/2A

With Arduino, 2 stepper drivers

Carriage DC-DC

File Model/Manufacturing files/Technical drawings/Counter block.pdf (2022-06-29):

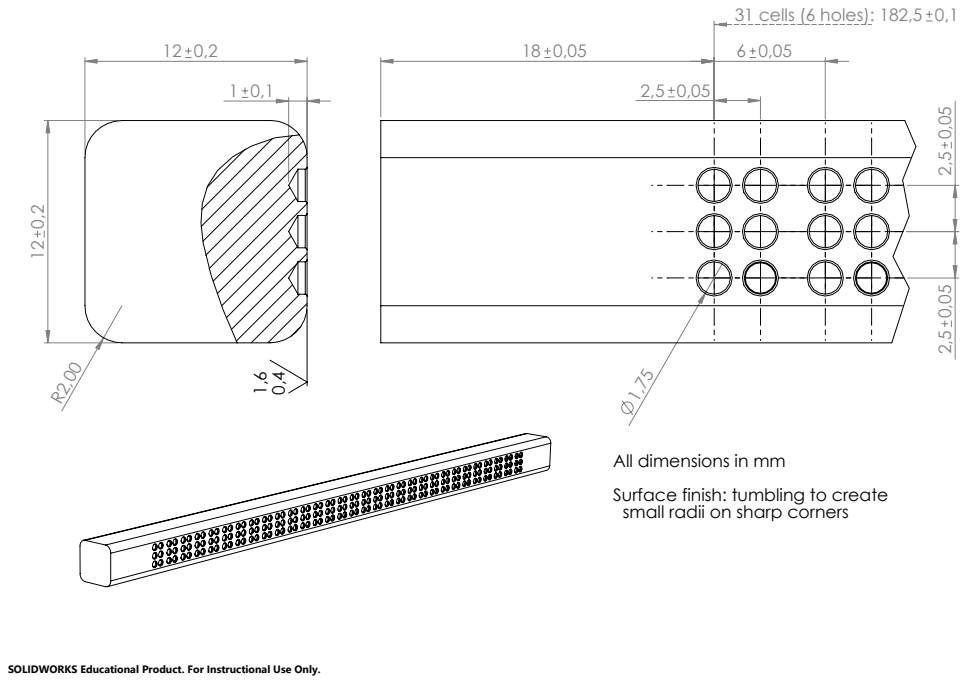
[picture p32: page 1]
31 cells (6 holes): 182,5

All dimensions in mm
Surface finish: tumbling to create
small radii on sharp corners

SOLIDWORKS Educational Product. For Instructional Use Only.

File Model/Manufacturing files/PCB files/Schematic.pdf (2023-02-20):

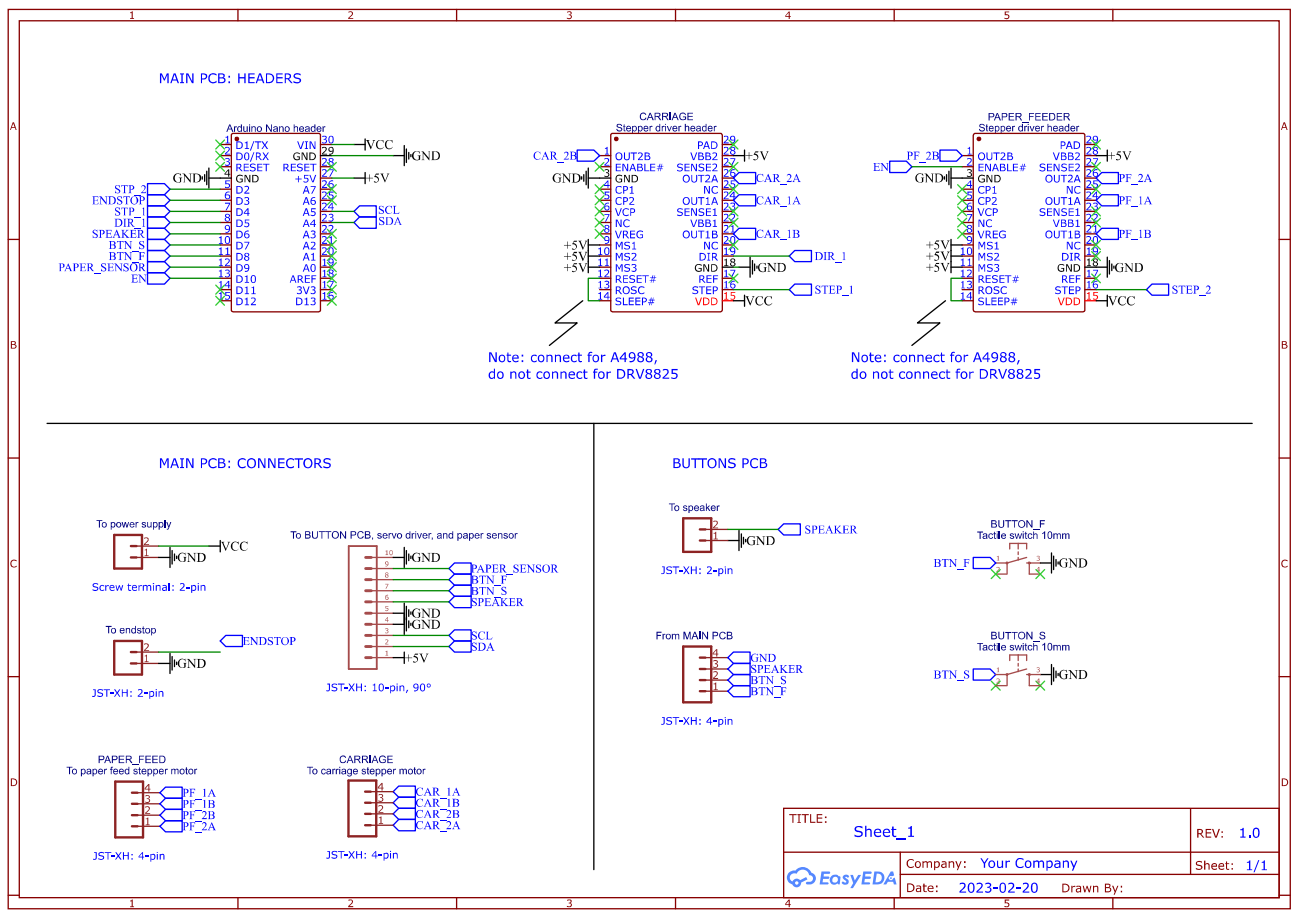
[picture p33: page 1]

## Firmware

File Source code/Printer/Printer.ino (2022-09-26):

// General setup:
#include <Arduino.h>
#include <Wire.h>
#include <Adafruit_PWMServoDriver.h>

enum states
{
    transmitting,
    printing
} activeState = transmitting;
uint8_t buffer[32];
bool homed = false;

// Setup for servos:
Adafruit_PWMServoDriver servos = Adafruit_PWMServoDriver();
uint16_t servosIdle[6] = {1400, 1600, 890, 1550, 1480, 1480};
uint16_t servosPressed[6] = {1240, 1410, 750, 1700, 1620, 1610};

// Setup for buttons:
#define BUTTON_S_PIN 8
#define BUTTON_F_PIN 7
#define PAPER_SENSOR_PIN 9
#define LIMIT_SWITCH_PIN 3

// Setup for speaker:
#define SPEAKER_PIN 6
enum pitches
{
    noteC3 = 131,
    noteA3 = 220,
    noteB3 = 247,
    noteD4 = 293,
    noteC5 = 523
};

/* MAIN SETUP */
void setup()
{
    Serial.begin(9600);

    // Initialize servos:
    servos.begin();
    servos.setOscillatorFrequency(27000000);
    servos.setPWMFreq(50);
    for (int i = 0; i < 6; i++)
    {
        servos.writeMicroseconds(i, servosIdle[i]);
    }

    // Initialize buttons:
    pinMode(BUTTON_S_PIN, INPUT_PULLUP);
    pinMode(BUTTON_F_PIN, INPUT_PULLUP);
    pinMode(PAPER_SENSOR_PIN, INPUT_PULLUP);
    pinMode(LIMIT_SWITCH_PIN, INPUT_PULLUP);

    // Initialize steppers:
    pinMode(5, OUTPUT);     // carriage direction
    pinMode(4, OUTPUT);     // carriage step
    pinMode(2, OUTPUT);     // feeder step
    digitalWrite(10, HIGH); // turn off feeder

    // Initialize speaker:
    pinMode(SPEAKER_PIN, OUTPUT);
    tone(SPEAKER_PIN, noteC5, 150);
    wait(200000);
    tone(SPEAKER_PIN, noteD4, 200);
    wait(200000);
}

/* MAIN LOOP */
void loop()
{
    if (activeState == transmitting)
    {
        // Send "Ready to receive line":
        Serial.write("1");
        // Read up to 32 characters from serial:
        for (int i = 0; i < 32; i++)
        {
            // Wait for computer to receive data, while checking button "F":
            while (!Serial.available())
            {
                // Next line in case button F is pressed:
                if (!digitalRead(BUTTON_F_PIN))
                    nextY();

                // Take a breathe to prevent overheating in idle state:
                wait(50000);
            }

            // Read single char:
            buffer[i] = Serial.read();
            delay(1);

            // In case of new line (0b01000000) or end of file (0b01000001):
            if (buffer[i] >= 0b01000000)
            {
                Serial.write(buffer, 32);
                // Change state to "printing":
                activeState = printing;

                // Break out of for-loop (mandatory):
                break;
            }
        }
    }
    else
    { // activeState == printing
        // Home if not yet homed:
        if (!homed)
            home();

        // If no paper detected, feed until new paper inserted:
        nextPaper();

        // Print entire line:
        for (int i = 0; i < 32; i++)
        {
            // Print single char:
            if (buffer[i] < 0b01000000)
            {
                // Print single char, except spaces:
                if (buffer[i] != 0b0)
                    printChar(buffer[i]);

                // Move to next position or break out of for-loop:
                if (buffer[i + 1] < 0b01000000)
                {
                    nextX();
                }
            }
            else
            {
                // In case of end of file, stop printjob:
                break;
            }
        }

        // Move to position 0:
        if (!homed)
            home();

        // Next line:
        nextY();

        // Empty the buffer:
        memset(buffer, 0, sizeof(buffer));

        // Send ready to receive new line:
        activeState = transmitting;
    }
}

void wait(uint64_t delayTime)
{
    // Starting time:
    uint64_t startTime = micros();

    // Wait while reading button "S":
    while (startTime + delayTime > micros())
    {
        if (!digitalRead(BUTTON_S_PIN))
        {
            // Send "printer halted":
            Serial.write("2");

            // Wait until button is released:
            while (!digitalRead(BUTTON_S_PIN))
                ;

            // Speaker: "Terminated":
            tone(SPEAKER_PIN, noteC3, 300);
            wait(500000);
            tone(SPEAKER_PIN, noteC3, 600);

            // Stop everything until hard reset:
            while (true)
            {
            }
        }
    }
}

/* MOVEMENT FUNCTIONS */
void nextX()
{
    // Set to not homed:
    homed = false;

    // Set direction to positive:
    digitalWrite(5, LOW);

    // Take 480 steps:
    for (uint16_t i = 0; i < 480; i++)
    {
        PORTD = PORTD | B00010000;
        wait(150);
        PORTD = PORTD & B11101111;
        wait(150);
    }
}
void nextY()
{
    // Turn on stepper motor:
    digitalWrite(10, LOW);
    wait(200000);

    // Go to next line
    for (uint16_t i = 0; i < 1300; i++)
    {
        PORTD = PORTD | B00000100;
        wait(100);
        PORTD = PORTD & B11111011;
        wait(100);
    }

    // Turn off stepper motor
    wait(10000);
    digitalWrite(10, HIGH);
    wait(200000);
}
void nextPaper()
{
    // When no paper detected on next line:
    if ((PINB & 2) != 0)
    { // fast !digitalRead(9)
        // Speaker: "Enter new paper":
        tone(SPEAKER_PIN, noteB3, 150);
        wait(200000);
        tone(SPEAKER_PIN, noteB3, 150);
        wait(200000);
        tone(SPEAKER_PIN, noteA3, 200);

        // Turn on stepper motor:
        digitalWrite(10, LOW);
        wait(200000);

        // Outfeed (optional) previous paper:
        for (uint16_t i = 0; i < 8111; i++)
        {
            PORTD = PORTD | B00000100;
            wait(100);
            PORTD = PORTD & B11111011;
            wait(100);
        }

        // Feed until paper sensor is triggered:
        while ((PINB & 2) != 0)
        { // fast !digitalRead(9)
            PORTD = PORTD | B00000100;
            wait(100);
            PORTD = PORTD & B11111011;
            wait(100);
        }

        // Speaker: "New paper detected":
        tone(SPEAKER_PIN, noteA3, 200);
        wait(150000);
        tone(SPEAKER_PIN, noteB3, 200);

        // Feed in:
        for (uint16_t i = 0; i < 4340; i++)
        {
            PORTD = PORTD | B00000100;
            wait(100);
            PORTD = PORTD & B11111011;
            wait(100);
        }

        // Turn off stepper motor
        digitalWrite(10, HIGH);
        wait(200000);
    }
}
void home()
{
    if (!digitalRead(LIMIT_SWITCH_PIN))
    { // if limit switch triggered
        // Set direction to positive:
        digitalWrite(5, LOW);

        // Take steps until endstop is no longer triggered
        while (!digitalRead(LIMIT_SWITCH_PIN))
        {
            PORTD = PORTD | B00010000;
            wait(50);
            PORTD = PORTD & B11101111;
            wait(50);
        }
    }
    else
    {
        // Set direction to negative:
        digitalWrite(5, HIGH);

        // Take steps until endstop is triggered:
        while (digitalRead(LIMIT_SWITCH_PIN))
        {
            PORTD = PORTD | B00010000;
            wait(50);
            PORTD = PORTD & B11101111;
            wait(50);
        }
    }

    // Set direction to positive:
    digitalWrite(5, LOW);

    // Take a couple of steps:
    for (uint16_t i = 0; i < 500; i++)
    {
        PORTD = PORTD | B00010000;
        wait(70);
        PORTD = PORTD & B11101111;
        wait(70);
    }

    // Set direction to negative:
    digitalWrite(5, HIGH);

    // Home slowly:
    while (digitalRead(LIMIT_SWITCH_PIN))
    {
        PORTD = PORTD | B00010000;
        wait(200);
        PORTD = PORTD & B11101111;
        wait(200);
    }

    // Set direction to positive:
    digitalWrite(5, LOW);

    // Move to first character position (offset):
    for (uint16_t i = 0; i < 10; i++)
    {
        PORTD = PORTD | B00010000;
        wait(150);
        PORTD = PORTD & B11101111;
        wait(150);
    }

    // Set homed:
    homed = true;
}

/* PRINTHEAD FUNCTIONS */
void printChar(uint8_t character)
{
    // Wake up servo driver (for power distribution):
    servos.wakeup();
    wait(10000);

    // set all servos:
    for (uint8_t i = 0; i < 6; i++)
    {
        // Iterate through each pin in 6-digit input:
        if (character >> i & 0b1)
        {
            // Press down single servo:
            servos.writeMicroseconds(i, servosPressed[i]);
        }
        else
        {
            // Keep non-active servo idle:
            servos.writeMicroseconds(i, servosIdle[i]);
        }
    }

    // Wait for pins to go up:
    wait(500000);

    // Release all servos:
    for (uint8_t i = 0; i < 6; i++)
    {
        servos.writeMicroseconds(i, servosIdle[i]);
    }

    // Wait for pins to go down:
    wait(200000);

    // Turn off servo driver:
    servos.sleep();
    wait(10000);
}

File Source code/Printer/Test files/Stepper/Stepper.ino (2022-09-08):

int stepCarrPin = 4;
int stepFeedPin = 2;
int dirCarrPin = 5;
int endstopPin = 3;
uint64_t speedDelay = 63;

void setup(){
  pinMode(stepCarrPin, OUTPUT);
  pinMode(stepFeedPin, OUTPUT);
  pinMode(dirCarrPin, OUTPUT);
  pinMode(endstopPin, INPUT_PULLUP);

  // First home the carriage
  PORTD = PORTD | B00100000;
  while((PIND & 0b00001000) != 0){
    PORTD = PORTD | B00010000;
    waitMicroseconds(speedDelay);
    PORTD = PORTD & B11101111;
    waitMicroseconds(speedDelay);
  }
}

void loop(){
  PORTD = PORTD & B11011111;
  for(int i = 0; i < 30; i++){
    delay(300);
    for(int j = 0; j < 480; j++){
    PORTD = PORTD | B00010000;
    waitMicroseconds(speedDelay);
    PORTD = PORTD & B11101111;
    waitMicroseconds(speedDelay);
  }
  }
  delay(300);
  PORTD = PORTD | B00100000;
  while((PIND & 0b00001000) != 0){
    PORTD = PORTD | B00010000;
    waitMicroseconds(speedDelay);
    PORTD = PORTD & B11101111;
    waitMicroseconds(speedDelay);
  }
}

void waitMicroseconds(uint64_t delayTime){
    // Starting time:
    uint64_t startTime = micros();

    // Wait while reading button "S":
    while (startTime + delayTime > micros()){}
}

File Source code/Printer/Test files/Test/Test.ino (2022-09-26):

#include "Pins.h"
#include "Stepper.h"
#include "Tone.h"

enum states
{
	transmitting,
	printing
} activeState = transmitting;
uint8_t buffer[32];

BraillePin braillePins[] = {
	BraillePin(3, 90, 100),	 // upper left
	BraillePin(5, 90, 100),	 // middle left
	BraillePin(6, 90, 100),	 // lower left
	BraillePin(9, 100, 90),	 // upper right
	BraillePin(10, 100, 90), // middle right
	BraillePin(11, 100, 90)	 // lower right
};

Stepper stepperX(4, 5);
Stepper stepperY(2);

void printChar(uint8_t character)
{
	// Push up concerning pins:
	for (uint8_t i = 0; i < 6; i++)
	{
		if (character >> i & 1)
		{
			braillePins[i].pinUp();
		}
	}
	wait(500000);

	// Release all pins:
	for (BraillePin bp : braillePins)
		bp.pinDown();
	wait(200000);
}

void wait(uint64_t delayTime)
{
	// Set starting time:
	uint64_t startTime = micros();

	while (startTime + delayTime > micros())
	{
		// If button S triggered:
		if (!digitalRead(8))
		{
			// Send "Stop":
			Serial.write(0x32);

			// Turn off power from stepper:
			stepperY.empower(false);

			signal(emergencyStop);

			// Stop everything:
			while (true)
				;
		}
	}
}

void setup()
{
	// Initialize pins:
	for (BraillePin braillePin : braillePins)
		braillePin.initialize();

	pinMode(2, OUTPUT);		  // feed step
	pinMode(3, INPUT_PULLUP); // limit switch
	pinMode(4, OUTPUT);		  // carr step
	pinMode(5, OUTPUT);		  // carr dir
	pinMode(6, OUTPUT);		  // speaker
	pinMode(7, INPUT_PULLUP); // button F
	pinMode(8, INPUT_PULLUP); // button S
	pinMode(9, INPUT_PULLUP); // paper sensor

	// Initialize serial:
	Serial.begin(9600);
	while (!Serial)
		;

	signal(boot);
}

void loop()
{
	if (activeState == transmitting)
	{
		Serial.write(0x31);
		for (uint8_t i = 0; i < 32; i++)
		{
			while (!Serial.available())
			{
				wait(50000);
			}

			buffer[i] = Serial.read();

			if (buffer[i] >= 0b01000000)
			{
				activeState = printing;
				break;
			}
		}
	}
	else // activeState == printing
	{
		stepperX.home();

		if (!digitalRead(9)) // paper sensor
			stepperY.nextPaper();

		for (uint8_t i : buffer)
		{
			if (buffer[i] < 0b01000000)
			{
				if (buffer[i] != 0)
					printChar(buffer[i]);

				if (buffer[i + 1] < 0b01000000)
				{
					stepperX.homed = false;
					stepperX.takeStep(480, 150);
				}
			}
			else
			{
				break;
			}
		}

		stepperX.home();

		stepperY.empower(true);
		stepperY.takeStep(1300, 100);
		stepperY.empower(false);

		memset(buffer, 0, sizeof(buffer));

		activeState = transmitting;
	}
}

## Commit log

2022-06-28 Updated BOM
    [BOM.xlsx]
2022-06-29 Updated CAD file
    [Brailleprinter.SLDASM, Button PCB.SLDASM, Carriage.SLDASM, Counter block.SLDPRT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]
2022-06-29 Added techn. draw. and restructured folders
    [Cap.STL, Carriage_part1.STL, Carriage_part2.STL, Counter block.SLDDRW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]
2022-06-29 Added README for PCB files
2022-06-29 Added PDF of technical drawing
    [Counter block.SLDDRW]
2022-06-29 Forgot 2 printable files
    [ButtonF.STL, ButtonS.STL]
2022-06-29 Added printing instructions file
2022-06-29 Update CAD file
    [Brailleprinter.SLDASM]
2022-06-29 Fixed mistake button assembly
    [Button PCB.SLDASM, ButtonF.SLDPRT, ButtonF.STL, ButtonS.SLDPRT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]
2022-06-30 Update counter block manufacturing
    [Brailleprinter.SLDASM, Button PCB.SLDASM, Carriage.SLDASM, Counter block.STEP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]
2022-07-01 Added different fits for buttons
    [ButtonF.SLDPRT, ButtonF.STL, ButtonS.SLDPRT, ButtonS.STL]
2022-07-01 Updated predrill holes M4 to 3.3mm
    [Frame plate.SLDPRT, Frame plate.dxf]
2022-07-01 Added configurations to Counter block
    [Brailleprinter.SLDASM, Button PCB.SLDASM, Carriage.SLDASM, Counter block.SLDPRT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]
2022-07-05 Wider tolerance on carriage
    [Brailleprinter.SLDASM, Button PCB.SLDASM, Carriage.SLDASM, Carriage.SLDPRT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]
2022-07-06 Update Carriage STL
    [Carriage_part1.STL]
2022-07-09 Add .gitignore file
    [Brailleprinter.SLDASM, Button PCB.SLDASM, Cable carrier.SLDPRT, Carriage.SLDASM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]
2022-07-11 Add drill guide files
    [Brailleprinter.SLDASM, Button PCB.SLDASM, Cable carrier.SLDPRT, Carriage.SLDASM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]
2022-08-09 Update CAD model, switch to SW 2022 (SE)
    [2GT driving pulley.SLDPRT, Brailleprinter.SLDASM, Button PCB.SLDASM, Button PCB.SLDPRT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]
2022-08-09 Test files Arduino
2022-08-10 Changed to closed loop belt
    [BOM.xlsx, Brailleprinter.SLDASM, Frame plate.SLDPRT, Frame.SLDASM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]
2022-08-11 Update Frame plate DXF file
    [Frame plate.SLDPRT, Frame plate.dxf]
2022-08-11 SW file fix
    [Brailleprinter.SLDASM, Frame.SLDASM]
2022-08-13 Added testfiles Arduino, updated pins on PCB and code
2022-08-16 Optimized paper feed mechanism
    [2GT driving pulley.SLDPRT, BOM.xlsx, Brailleprinter.SLDASM, Cable carrier.SLDPRT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]
2022-08-17 Fixed Electronics box - extra wiring space
    [Brailleprinter.SLDASM, Cable carrier.SLDPRT, Carriage.SLDASM, Electronic box.SLDASM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]
2022-08-23 Added tools for manufacturing
    [Drill guide carriage.STL, Drill guide frame.STL, Rubber ring guide.SLDPRT, Rubber ring guide.STL]
2022-09-05 Added pinout file, changed STL whoopsie
    [Brailleprinter.SLDASM, Paper feeding.SLDASM, Side block.SLDPRT, Side block_part1.STL]
2022-09-06 Working on stepper settings
2022-09-08 Reworked Arduino code, added calculations sheet
    Communication between computer and Arduino did not do the job. Still don't know why. Cleaned the code and uploaded step by step, and now it all works. Still don't know why.
    [Calculations.xlsx]
2022-09-08 Small update on 3D model
    [Brailleprinter.SLDASM, Cable carrier.SLDPRT, Carriage.SLDASM]
2022-09-10 Update counter block
    [Brailleprinter.SLDASM, Counter block.SLDPRT, Paper feeding.SLDASM]
2022-09-13 Temporary assembly fix
    [Brailleprinter.SLDASM, Electronic box.SLDASM, Electronic box.SLDPRT, Paper feeding.SLDASM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]
2022-09-15 Update for Peter
    [Brailleprinter.SLDASM, Calculations.xlsx]
2023-02-20 Add STEP file
    [Brailleprinter.SLDASM]
